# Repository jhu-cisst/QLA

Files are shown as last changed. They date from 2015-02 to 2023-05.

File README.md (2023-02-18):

# QLA
Design files for Quad Linear Amplifier (QLA) board

* `QLA.PrjPCB`: Altium Designer project file
* `Snn.SchDoc`: schematics (Altium Designer format)
* `Snn.Harness`: signal harnesses (Altium Designer format)
* `AMP.PcbDoc`: PCB layout (Altium Designer format)
* `QLA-Schematics.pdf`: PDF of schematics
* `QLA-BOM.xls`: Bill of Materials (Microsoft Excel format)
* `QLA-HeatSink.pdf`: PDF of heat sink drawing
* `QLA-PCB-Fabrication.zip`: PCB fabrication (Gerber) files
* `QLA-Assembly.zip`: PCB assembly files (e.g., paste masks, pick-and-place)
 
## Release Notes

* Rev 1.1: Build #0 (5 board pilot run)
* Rev 1.2: Build #1 (44 boards)
  * Deleted trace from Q15A (MOSFET) to U39B (OPA549) to avoid glitches at power-up (on all 4 channels)
  * Added J11 to enable connection to remote LED panel
* Rev 1.3 (PCB silkscreen is Rev 1.2): Build #2 (68 boards), Build #3 (72 boards), Build #4 (80 boards)
  * Changed relay (U31) from +12V to +5V to avoid rework needed to bring external +12V to board
  * Fixed silkscreen for Pot2 and Pot3 test points (they were swapped)
  * Changed R52 to 0 Ohms (Rev 1.1 and 1.2 boards were reworked accordingly)
  * Added screwlocks (Female, 4-40, 0.185") to DB9 connector
  * Design files indicate Rev 1.3, but manufactured boards show Rev 1.2; boards can be distinguished by looking at relay (U31)
* Rev 1.4: Build #5 (92 boards)
  * Changed digital outputs from open-drain MOSFETs to bi-directional bus transceivers (74LVC2T45) with 5V output; direction controlled by FPGA IO1-5 and IO1-6. Proper operation requires FPGA Firmware Rev 5+
  * Added feedback of motor voltage fault (from LT4356) on FPGA IO1-7
  * Grounded heatsink on PCB
  * Added plated slots for soldering 68-pin connector tabs
  * Moved Q13, Q14 and updated PCB pads to facilitate assembly
* Rev 1.4a: Build #6 (75 boards)
  * Increased acceptable range of motor supply voltage from 11.2V-50.2V to 10.5V-52.7V (values are approximate)
    * Changed R33, R34 to raise LT4356 maximum voltage from ~51.25V to ~52.7V
    * Changed R27, R28 to set MV_GOOD window comparator thresholds to 10.5V and 52.8V
  * Added transorb SMAJ64CA on back side of connector J5, between pins 2 and 3, to limit flyback voltages on motor power supply (especially with 48V supply)
* Rev 1.4b: Build #7 (120 boards), Build #8 (80 boards)
  * Changed pot filter cutoff frequency from 60 Hz to 5 kHz
    * Changed R1-8 from 39.2K to 464 Ohm
    * Allows faster reading of multiplexed signals (SUJ pots)
  * Fixed description of Q9-11,15 (30V instead of 20V)
* Rev 1.5: Build #9 (2 prototypes)
  * Added (open loop) motor voltage control as a software-selectable alternative to the existing (analog closed loop) motor current control
  * Added 10 digital I/O via an I/O expander (U41, Max7317):
    * 4 digital outputs to select between motor voltage control (0) or motor current control (1) for each axis
    * 4 digital outputs to enable the follower OPA549 op amps that previously were always enabled
    * 1 digital input that indicates whether voltage is present on safety line
    * 1 digital input that can be used to measure the motor supply voltage
  * Increased analog filter cutoff frequency from 60 Hz to 42 kHz for motor current feedback to ADC
  * Added pads for transorb (D12) on back side of board (previously, was either not present or was soldered between connector pins)
  * Changes due to component availability issues:
    * Support use of 1 LTC2604 quad DAC instead of 4 LTC2601 single DACs; populate pulldown resistor R75 to indicate use of LTC2604
    * Support AD7694 as an alternative to LTC1864 ADC; this required the addition of voltage level translators (U44, U45)
    * Changed part number for 2.5V linear regulator (U32), which included a pinout change
    * Changed footprint for safety relay (U31)
    * Changed footprint for D7 (Schottky diode)
    * Several other part number changes that did not change pinout or package type
* Rev 1.6: Build #9 (98 boards)
  * Added tristate buffer (U46) to Max7317 output
  * Use OPA549 feedback cap (C74) for voltage control, in addition to current control, to prevent oscillation; increased C74 voltage rating from 16V to 100V and changed package from 0603 to 1206
  * Disconnected J2, pin 44, from GND (consistent with change to FPGA V3.1)

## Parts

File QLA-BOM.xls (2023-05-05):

 | Quad Linear Amplifier, Rev 1.6
 | Bill Of Materials
 | 2023-05-04
Revision: |  | 1.6
Seq | Qty. | Ref Des (Multi-4) | Description | Package | Manufacturer | Notes | Manufacturer Part # | Distributor | Distributor Part # | Avcon Part # | Est. Unit $ | Extended Cost
1 | 5 | C1-4, C92 | CAP, 0.047uF, 10%, 25V, X7R, 0603 | 0603 | Kemet | 2 | C0603C473K3RAC7867 | Digikey | 399-C0603C473K3RAC7867CT-ND | 022-4734-71/603 | 0.04 | 0.20
2 | 20 | C5-8, C65-68 | CAP, 1000pF, 5%, 50V, NPO, 0603 | 0603 | MuRata | 2 | GRM1885C1H102JA01D | Digikey | 490-1451-1-ND | 022-1026-61/603 | 0.02 | 0.48
3 | 14 | C9-10, C69-71 | CAP 0.01uF, 10%, 50V, X7R, 0603 | 0603 | Kemet | 2 | C0603C103K5RACTU | Digikey | 399-1091-1-ND | 022-1036-71/603 | 0.04 | 0.56
4 | 2 | C11-12 | CAP, 10uF 20%, 6.3V, X5R, 0603 | 0603 | TDK | 2 | C1608X5R0J106M080AB | Digikey | 445-4112-1-ND | 022-1061-81/603 | 0.32 | 0.64
5 | 2 | C13-14 | CAP, 1.0uF 10% 16V X7R, 0603 | 0603 | TDK | 2 | C1608X7R1C105K080AC | Digikey | 445-1604-1-ND | 022-1052-71/603 | 0.04 | 0.09
6 | 1 | C15 | CAP, 220pF, 5%, 50V, NPO, 0603 | 0603 | Kemet | 2 | C0603C221J5GACTU | Digikey | 399-1066-1-ND | 022-2216-61/603 | 0.14 | 0.14
7 | 1 | C16 | CAP, 0.022uF, 10%, 50V, X7R, 0603 | 0603 | TDK | 2 | C1608X7R1H223K080AA | Digikey | 445-1312-1-ND | 022-2236-71/603 | 0.03 | 0.03
8 | 3 | C17-19 | CAP, 47uF, 20%, 10V, Polymer Tantalum, Cap-B | CAP-B | AVX | NS | TCJB476M010R0070 | Digikey | 478-3132-1-ND | 022-4761-85SMB | 1.10 | 3.30
9 | 4 | C20-23 | CAP, 150uF, 20%, 6.3V, Polymer Tantalum, Cap-B | CAP-B | AVX | NS | TCJB157M006R0070 | Digikey | 478-4921-1-ND | 022-1570-85SMB | 2.48 | 9.92
10 | 3 | C24, C94-95 | CAP, 2.2uF, 20%, 100V, X7S, 1206 | 1206 | TDK | 2 | C3216X7S2A225M | Digikey | 445-5208-1-ND | 022-2267-81SM | 1.21 | 3.63
11 | 1 | C25 | CAP, 68uF 10%, 25V, Low ESR Tant. "SpeedPower" | CAP-D | Kemet | NS | T495X686K025ATE200 T495X686K025ZTE200 | Digikey | 399-3908-1-ND | 022-6864-75SMD | 1.69 | 1.69
12 | 5 | C26, C85 | CAP, 220uF, 20%, 63V, Alum, Low ESR, 10mm Radial | CAP-10MM | Rubycon | NS, 12 | 63YXJ220M10X20 |  |  | 022-2210-86 | 0.73 | 3.65
13 | 83 | C27-64, C75-82, C87-88, C93, C96-105 | CAP, 0.1uF 10% 16V X7R, 0603 | 0603 | Kemet | 2 | C0603C104K4RACTU | Digikey | 399-1096-1-ND | 022-1042-71/603 | 0.02 | 1.66
14 | 4 | C72 | CAP, 0.068uF 10% 16V X7R, 0603 (25V) | 0603 | Kemet | 2 | C0603C683K3RAC7867 | Digikey | 399-C0603C683K3RAC7867CT-ND | 022-6832-71/603 | 0.03 | 0.14
15 | 4 | C73 | CAP, 2.2uF 10% 6.3V X7R, 0603 | 0603 | MuRata | 2 | GCM188R70J225KE22D | Digikey | 490-5316-1-ND | 022-2250-71/603 | 0.45 | 1.80
16 | 12 | C83-84, C91 | CAP, 0.1uF, 10%, 100V, X7R, 0805 | 0805 | Kemet | 2 | C0805C104K1RACTU | Digikey | 399-3486-1-ND | 022-1047-71/805 | 0.35 | 4.20
17 | 8 | C74, C86 | CAP, 0.1uF, 10%, 100V, X7R, 1206 | 1206 | Kemet | 2 | C1206C104K1RACTU | Digikey | 399-1805-1-ND | 022-1047-71SM | 0.30 | 2.40
18 | 4 | C89 | CAP, 200pF, 10%, 10V+, X7R, 0603 (50V) | 0603 | Samsung | 2 | CL10B201KB8NNNC | Digikey | 1276-1982-1-ND |  | 0.02 | 0.06
19 | 4 | C90 | CAP, 100pF, 10%, 10V+, X7R, 0603 | 0603 | Samsung | 2 | CL10B101KB8NFNC | Digikey | 1276-1908-1-ND |  | 0.02 | 0.08
20 | 2 | D1-2 | LED, Dual, Red/Green | LED-3MM-QUAD | Kingbright | NS | WP130WCP/2EGW | Digikey | 754-1205-ND | 024-6382-00 | 0.97 | 1.94
21 | 1 | D3 | LED, Quad, Green | LED-3MM-QUAD | Kingbright | NS | WP914CK/4GDT | Digikey | 754-1286-ND | 024-6383-00 | 1.25 | 1.25
22 | 1 | D4 | DIODE, Dual Zener, 6.8V, SOT-23, DZ23C6V8 | SOT-23 | Vishay |  | AZ23C6V8-E3-08 | Mouser | 78-AZ23C6V8-E3-08 | 024-0514-SM | 0.15 | 0.15
23 | 2 | D5-6 | DIODE, 75V, 150mA, 1N4148WS, SOD-323 | SOD-323 | Diodes Inc. |  | 1N4148WS-7-F | Digikey | 1N4148WS-FDICT-ND | 024-0244-SM | 0.18 | 0.36
24 | 1 | D7 | DIODE, Schottky, 60V, 1A | SMP | Vishay |  | SS1P6L-M3/84A | Digikey | SS1P6L-M3/84AGICT-ND |  | 0.21 | 0.21
25 | 16 | D8-11 | DIODE, Schottky, 60V, 5A, PDS560 | PowerDI-5 | Diodes Inc. |  | PDS560-13 | Digikey | PDS560DICT-ND | 024-0362-SM | 1.36 | 21.76
26 | 1 | D12 | DIODE, TVS (Transorb) | SMA | Bourns | 2, 8 | SMAJ64CA | Mouser | 576-SMAJ64CA |  | 0.28 | 0.28
27 | 1 | D13 | DIODE, Zener, 36V, 1W | PowerDI-123 | Diodes Inc. |  | DFLZ36-7 | Digikey | DFLZ36-7DICT-ND |  | 0.30 | 0.30
28 | 2 | J1-2 | CONN, Header, 2x22 Pos, Vertical, 2MM. | HDR-22x2-2MM | Samtec |  | TMM-122-03-L-D | Samtec | TMM-122-03-L-D | 026-0846-00 | 2.00 | 4.00
29 | 1 | J3 | CONN, SCSI/VHDCI, 68 Pin, RA | CONN-VHDCI | TE Conn | NS | 5796055-1 | Mouser | 571-5796055-1 | 026-1137-00 | 15.88 | 15.88
30 | 1 | J4 | CONNECTOR, DB-9 Female, High Current | DB9F | Tyco | NS | 5205866-1 | Digikey | A32065-ND | 026-0862-00 | 17.04 | 17.04
31 | 1 | J5 | CONN, Receptacle, 4 Pos, 3.8mm Vertical | WM-BL381-4 | Weidmuller |  | 1793810000 | Digikey | 281-1959-ND | 026-1138-00 | 1.55 | 1.55
32 | 3 | J6-8 | CONN, Header, 2 Pos, Vertical 0.100 | TH | Tyco | 2 | 640456-2 | Digikey | A1921-ND | 026-0080-00 | 0.30 | 0.90
33 | 2 | J9-10 | CONN, Header, 3 Pos, Vertical 0.100 | TH | Tyco | 2 | 640456-3 | Digikey | A19470-ND | 026-0083-00 | 0.34 | 0.68
34 | 1 | J11 | CONN, Header, 2x6 Pos, Vertical, 2MM. | TH | Hirose |  | DF11-12DP-2DSA(24) | Digikey | H10233-ND | 026-0840-00 | 0.92 | 0.92
35 | 1 | L1 | INDUCTOR, 100uH 20%, 1.9A | DR127 | Cooper | NS | DR127-101-R | Digikey | 513-1038-1-ND | 023-0178-SM | 1.74 | 1.74
36 | 3 | Q1-2, Q12 | Transistor, NPN, 160V, MMBT5551L | SOT-23 | Diodes Inc. | 2 | MMBT5551-7-F | Digikey | MMBT5551-FDICT-ND | 024-1193-SM | 0.43 | 1.29
37 | 0 | Q3-4 | Designator not used |  |  |  |  |  |  |  | 0.00 | 0.00
38 | 4 | Q5-8 | MOSFET, Pair N/P-Chan, 50V, 115mA, BSS8402 | SC70-6 | Rohm | 13 | US6M2 | Mouser | 755-US6M2GTR | 024-2199-SM | 0.30 | 1.20
39 | 7 | Q9-11, Q15 | MOSFET, Dual N-Chan, 30V (20V) | SOT-363 | Vishay | 2, 9 | SQ1912EH | Digikey | Q1912EH-T1_GE3CT-ND | 024-2190-SM | 0.19 | 1.33
40 | 2 | Q13-14 | MOSFET, N-Chan, 100V, 160A (200A) | TO-263-7 | On Semi | 10 | FDB0300N1007L | Mouser | 512-FDB0300N1007L | 024-2197-SM | 4.47 | 8.94
41 | 8 | R1-8 | RES, 464, 1%, 1/10W, 0603 | 0603 | Generic | 2, 15 | RC0603FR-07464RL | Digikey | 311-464HRCT-ND |  | 0.01 | 0.08
42 | 12 | R9-12, R56, R76-79 | RES, 100, 1%, 1/10W, 0603 | 0603 | Generic | 2 |  | Digikey | 541-100HCT | 020-1000-51/603 | 0.04 | 0.48
43 | 10 | R13-22 | RES, 150, 1%, 1/10W, 0603 | 0603 | Generic | 2 |  | Digikey | 541-150HCT | 020-1500-51/603 | 0.04 | 0.40
44 | 6 | R23-26, R68, R75 | RES, 1.00K, 1%, 1/10W, 0603 | 0603 | Generic | 2 |  | Digikey | 541-1.00KHCT | 020-1001-51/603 | 0.04 | 0.24
45 | 1 | R27 | RES, 127K, 1%, 1/10W, 0603 | 0603 | Generic | 2 |  | Digikey | 541-127KHCT | 020-1273-51/603 | 0.04 | 0.04
46 | 2 | R28-29 | RES, 4.02K, 1%, 1/10W, 0603 | 0603 | Generic | 2 |  | Digikey | 541-4.02KHCT | 020-4021-51/603 | 0.04 | 0.08
47 | 1 | R30 | RES, 2.21K, 1%, 1/10W, 0603 | 0603 | Generic | 2 |  | Digikey | 541-2.21KHCT | 020-2211-51/603 | 0.04 | 0.04
48 | 1 | R31 | RES, 8.87K, 1%, 1/10W, 0603 | 0603 | Generic | 2 |  | Digikey | 541-8.87KHCT | 020-8871-51/603 | 0.04 | 0.04
49 | 23 | R32, R40-44, R71-72 | RES, 10.0K, 1%, 1/10W, 0603 | 0603 | Generic | 2 |  | Digikey | 541-10.0KHCT | 020-1002-51/603 | 0.04 | 0.92
50 | 1 | R33 | RES, 2.43K, 0.1%, 1/10W, 0603 | 0603 | Generic | 2 |  | Digikey | RG16P2.43KBCT-ND |  | 0.36 | 0.36
51 | 1 | R34 | RES, 100K, 0.1%, 1/10W, 0603 | 0603 | Generic | 2 |  | Digikey | RG16P100KBCT-ND |  | 0.34 | 0.34
52 | 1 | R35 | RES, 1.00M, 1%, 1/10W, 0603 | 0603 | Generic | 2 |  | Digikey | 541-1.00MHCT | 020-1004-51/603 | 0.04 | 0.04
53 | 2 | R36-37 | RES, 10.0, 1%, 1/10W, 0603 | 0603 | Generic | 2 |  | Digikey | 541-10.0HCT | 020-1009-51/603 | 0.04 | 0.08
54 | 2 | R38-39 | RES, 0.006, 1%, 1W, 2512 | R2512 | Yageo |  | PF2512FKF070R006L | Digikey | 311-0.006AGCT-ND | 020-6007-54/251 | 0.88 | 1.76
55 | 16 | R45-46, R54-55 | RES, 26.7K, 1%, 1/10W, 0603 | 0603 | Generic | 2 |  | Digikey | 541-26.7KHCT | 020-2672-51/603 | 0.04 | 0.64
56 | 8 | R47, R49 | RES, 182K, 1%, 1/10W, 0603 | 0603 | Generic |  |  | Digikey | P182KHCT-ND |  | 0.02 | 0.15
57 | 6 | R48, R52-53 | RES, 4.99K, 1%, 1/10W, 0603 | 0603 | Generic | 2 |  | Digikey | 541-4.99KHCT | 020-4991-51/603 | 0.04 | 0.24
58 | 8 | R50-51 | RES, 62.0, 0.1%, 1/10W, 0603 | 0603 | Susumu | NS | RG1608P-620-B-T5 | Digikey | RG16P62.0BCT-ND | 020-6209-21/603 | 0.53 | 4.24
59 | 9 | R57-58, R69 | RES, 20.0K, 1%, 1/10W, 0603 | 0603 | Generic | 2 |  | Digikey | 541-20.0KHCT | 020-2002-51/603 | 0.04 | 0.36
60 | 8 | R59-60 | RES, 20.0K, 0.1%, 1/10W, 0603 | 0603 | Susumu | 2 | RG1608P-203-B-T5 | Digikey | RG16P20.0KBCT-ND | 020-2002-21/603 | 0.40 | 3.20
61 | 4 | R61 | RES, 6.04K, 1%, 1/10W, 0603 | 0603 | Generic | 2 |  | Digikey | 541-6.04KHCT | 020-6041-51/603 | 0.04 | 0.16
62 | 4 | R62 | RES, 0.20 Ohm, 1%, 30W, TO-220 | TO-220 | Caddock | 3 | MP930-0.20-1% | Digikey | MP930-0.20F-ND | 020-2009-50 | 5.23 | 20.92
63 | 4 | R63 | RES, 4.7, 5%, 1/2W, Carbon Composite | R-1/2W | TE Conn | 2 | CBT50J4R7 | Mouser | 279-CBT50J4R7 | 020-4708-63 | 0.22 | 0.88
64 | 4 | R64-67 | RES, 100, 1%, 1/4W, 1206 | 1206 | Generic | 2 |  | Digikey | 541-100FCT | New Part | 0.04 | 0.16
65 | 1 | R70 | RES, 1.5K, 5%, 1/2W, 0805 | 0805 | Generic | 2 | ERJ-P06J152V | Digikey | P1.5KADCT-ND |  | 0.04 | 0.04
66 | 2 | R73-74 | RES, 49.9K, 1%, 1/10W, 0603 | 0603 | Generic |  |  | Digikey | RMCF0603FT49K9CT-ND |  | 0.01 | 0.01
67 | 5 | RN1-5 | RES ARRAY, 1.0K, 4 DIS, 5%, SM 0.032 | R-SM-8/32 | CTS | 2 | 742C083102JPTR | Digikey | 742C083102JPCT-ND | 020-1001-6RASM | 0.02 | 0.10
68 | 7 | RN6-9, RN13-15 | RES ARRAY, 10K, 4 DIS, 5%, SM 0.032 | R-SM-8/32 | CTS | 2 | 742C083103JPTR | Digikey | 742C083103JPCT-ND | 020-1002-6RASM | 0.02 | 0.14
69 | 3 | RN10-12 | RES ARRAY, 100, 4 DIS, 5%, SM 0.032 | R-SM-8/32 | CTS | 2 | 742C083101JPTR | Digikey | 742C083101JPCT-ND | 020-1000-6RASM | 0.02 | 0.06
70 | 1 | U1 | IC, EEPROM, 128Kbit, 25xx128 (xx=AA or LC) | TSSOP-8 | Microchip |  | 25xx128-I/ST (xx=AA or LC) | Digikey | 25LC128T-I/STCT-ND | 024-2620-SM | 1.14 | 1.14
71 | 1 | U2 | IC, Dual Power Switch, 500mA, TPS2046 | SO-8 | TI |  | TPS2046BDR | Digikey | 296-17246-1-ND | 024-3614-SM | 2.07 | 2.07
72 | 6 | U3-4, U36 | IC, Op-Amp, Dual | MSOP-8 | Microchip | 14 | MCP6V87T-E/MS | Digikey | 150-MCP6V87T-E/MSCT-ND | 024-6327-SM | 1.52 | 9.09
73 | 8 | U5-8, U34 | IC, ADC, 16 Bit | MSOP-8 | Analog Devices | 16 | AD7694xRM[Z] (x=A or B) | Digikey | AD7694ARMZ-ND |  | 15.19 | 121.48
74 | 4 | U9-10, U13-14 | IC, Dual Schmit Trig. Buffer, 5V Input, 74LVC2G17 | SOT-23-6 | On Semi | 2 | SN74LVC2G17DBVR | Digikey | 296-13012-1-ND | 024-3615-SM | 0.66 | 2.64
75 | 4 | U11-12, U44-45 | IC, 2-bit, Bus tranceiver/translator, 74LVC2T45 | US-8 | TI |  | SN74LVC2T45DCUR | Digikey | 296-17014-1-ND | New Part | 0.70 | 2.80
76 | 1 | U15 | IC, Linear Regulator, 4.5V, 150mA, LP2985A-4.5 | SOT-23-5 | National Semi. |  | LP2985AIM5-4.5/NOPB | Digikey | LP2985AIM5-4.5CT-ND | 024-2200-SM | 1.06 | 1.06
77 | 6 | U16-21 | IC, Quad Differential Receiver, AM26LV32 | SO-16 | TI |  | AM26LV32CD | Digikey | 296-6794-5-ND | 024-3618-SM | 1.34 | 8.04
78 | 1 | U22 | IC, Dual Comparator & Reference, LT6700-1 | SOT-23-6 | Linear Tech. | 1 | LT6700CS6-1#PBF | Linear Tech. | LT6700CS6-1#PBF | 024-2201-SM | 2.15 | 2.15
79 | 0 | U23-26 | IC, DAC, 16 Bit, Mid-Scale Startup, LTC2601-1 | DFN-10 | Linear Tech. | 1, 15 | LTC2601CDD-1#PBF | Linear Tech. | LTC2601CDD-1#PBF | 024-3616-SM | 3.60 | 0.00
80 | 1 | U27 | IC, Step Down DC-DC converter, 1.5A, LT1766 | TSSOP-16 | Linear Tech. | 1 | LT1766EFE#PBF | Linear Tech. | LT1766EFE#PBF | 024-2622-SM | 5.36 | 5.36
81 | 1 | U28 | IC, Over-Voltage Protection IC, LT4356-1 | MSOP-10 | Linear Tech. | 1 | LT4356CMS-1#PBF | Linear Tech. | LT4356CMS-1#PBF | 024-9188-SM | 5.36 | 5.36
82 | 2 | U29-30 | IC, Temperature to Frequency Converter, MAX6576 | SOT-23-6 | Maxim |  | MAX6576ZUT+T | Digikey | MAX6576ZUT+TTR-ND | 024-9307-SM | 2.73 | 5.46
83 | 1 | U31 | RELAY, 5V, DPDT | DIP | TE Conn |  | IM03TS | Digikey | PB1094-ND |  | 3.44 | 3.44
84 | 4 | U32 | IC, Linear Regulator, LDO, 2.5V, AP7333-SR | SOT-23 | Diodes Inc. |  | AP7333-25SRG-7 | Mouser | 621-AP7333-25SRG-7 |  | 0.23 | 0.93
85 | 4 | U33 | IC, 2-Input AND Gate, Single, 74LVC1G08 | SC70-5 | TI |  | SN74LVC1G08DCK | Digikey | 296-11602-1-ND | 024-3613-SM | 0.53 | 2.12
86 | 4 | U35 | IC, Op-Amp, Single, OPA990S | SOT-23-6 | TI |  | OPA990SIDBVR | TI | OPA990SIDBVR | New Part | 0.71 | 2.84
87 | 4 | U37 | IC, Differential Amplifier, LT1990 | SO-8 | Linear Tech. | 1 | LT1990CS8#PBF | Linear Tech. | LT1990CS8#PBF | 024-6316-SM | 1.65 | 6.60
88 | 8 | U38-39 | IC, Power Amplifier, OPA549T | POWER-11-T | TI | 3 | OPA549T | Digikey | OPA549T-ND | 024-9313-00 | 20.40 | 163.20
89 | 4 | U40 | IC, Analog SPDT Switch, TS5A3159A | SOT-23-6 | TI |  | TS5A3159ADBVT | Digikey | 296-27121-1-ND | New Part | 0.67 | 2.67
90 | 1 | U41 | IC, SPI I/O Expander | QSOP-16 | Maxim |  | MAX7317AEE+ | Mouser | 700-MAX7317AEET | New Part | 3.07 | 3.07
91 | 1 | U42 | IC, Comparator, Single, LMV331M | SOT-23-5 | TI | 2 | LMV331M5X/NOPB | Digikey | LMV331M5X/NOPBCT-ND | New Part | 0.62 | 0.62
92 | 1 | U43 | IC, DAC, Quad, 16 Bit, Mid-Scale Startup, LTC2604-1 | SSOP-16 | Linear Tech. | 1, 15 | LTC2604CGN-1#PBF | Digikey | LTC26014IGN-1#PBF-ND | New Part | 18.98 | 18.98
93 | 1 | U46 | IC, Tri-state Buffer, 74AHC1G125 | SOT-23-5 | TI | 2 | SN74AHC1G125DBV | TI | SN74AHC1G125DBVR | New Part | 0.06 | 0.06
94 | 1 |  | HEATSINK, Rev 4 |  |  |  |  | Columbus Machine Works |  | 039-0368-00 | 56.40 | 56.40
95 | 1 |  | PCB, Quad Linear Amplifier, Rev 1.5 |  |  |  |  | Ohio Circuits |  | 027-0435-00 | 35.00 | 35.00
96 | 17 |  | SCREW, 4-40 X 3/8" Pan Head |  |  | 4, 5 |  | McMaster-Carr | 90272A108 | 039-0178-00 | 0.18 | 3.09
97 | 2 |  | LOCKWASHER, #4 Ext. Tooth, Zinc Plated |  |  | 5 |  | McMaster-Carr | 91114A005 | 039-0251-00 | 0.55 | 1.09
98 | 2 |  | HEX NUT, 4-40 UNC-2B Stainless |  |  | 5 |  | McMaster-Carr | 91240A005 | 039-0043-30 | 0.43 | 0.86
99 | 2 |  | SCREWLOCK, Female, 4-40, 0.185" |  | Tyco | 6 | 5747877-3 | Digikey | A35224-ND | 039-0381-00 | 0.68 | 1.35
100 | 2 |  | SCREWLOCK, Female, M2 |  | TE Conn | 11 | 787004-3 | Mouser | 571-7870043 |  | 1.55 | 3.10
101 | 8 |  | Washer, 1/8" ID, 1/4" OD, Type B |  |  | 4, 7 |  | McMaster-Carr | 92217A360 | 039-0435-00 | 0.42 | 3.40
 |  |  |  |  |  |  |  |  |  | Estimated total Cost: |  | $628.06
Notes:
 | ● | Reference designators highlighted in green are replicated 4 times on the PCB, as UxxA, UxxB, UxxC and UxxD.
 | ● | Text highlighted in red is highlighted to draw attention to the value/parameter and does not carry any special meaning.
 | ● | Component prices shown are the best guess at the time of updating this BOM, assuming Qty ~100 boards. Actual prices may be higher or lower depending upon a number of factors.
 | ● | Unless specified otherwise, the only substitutions allowed are substituting identical part number parts from a different manufacturer.
 | NS | No substitutions of any kind are allowed.
 | 1 | For Linear Tech parts, it is acceptable to substitute I (industrial temp), E (extended temp) or H (high temp) rated parts.
 |  | The suffixes "TRM" and "TR" signify tape and reel styles. Parts with suffix TRM, suffix TR can be substituted as needed.
 |  | Other than as specified above, no other substitutions are allowed.
 | 2 | Any component in an identical package that meets or exceeds all the paramaters specified in the description can be substituted.
 | 3 | The component must be installed to the heat sink or a heat sink template before being soldered to the board.
 |  | Use Thermal Heat Sink Compound Type 120, Avcom P/N 043-0018-00
 | 4 | For attaching components to Heat Sink
 | 5 | For attaching DB9 to PCB (Qty 2: Screw, Lockwasher, Hex nut)
 | 6 | Screwlocks for DB9 connector
 | 7 | For attaching OPA549 to heat sink when using 4-40 screws
 | 8 | Soldered on back side of board, near connector J5
 | 9 | Previously used 30V rated parts: NXP PMGD175XNE (Digikey P/N 1727-2695-1-ND) and PMGD370XN (Digikey P/N 568-2367-1-ND); another alternative is ON Semiconductor NTJD4001NT1G (Digikey P/N NTJD4001NT1GOSCT-ND)
 | 10 | Previously used Infineon IPB039N10N3 (Mouser P/N 726-IPB039N10N3G); other possibilities are Infineon IRLS4030TRL7PP and (higher rated) IPB065N15N
 | 11 | Screwlocks for VHDCI (68-pin) connector
 | 12 | Previously used United Chem, ELXZ630ELL221MJ25S (Digikey P/N 565-2040-ND)
 | 13 | Previously used Diodes Inc. BSS8402DW-7-F (Digikey P/N BSS8402DW-FDICT-ND)
 | 14 | Previously used Linear Tech LTC6081CMS8#PBF
 | 15 | Populate either U43 (LTC2604) and R75 or U23-U26 (LTC2601)
 | 16 | Previously used Linear Tech LTC1864CMS8#PBF (Avcom P/N 024-2621-SM)
Component Counts:
 | C | 180
 | D | 25
 | J | 11
 | L | 1
 | Q | 16
 | R | 145
 | RN | 15
 | U | 68

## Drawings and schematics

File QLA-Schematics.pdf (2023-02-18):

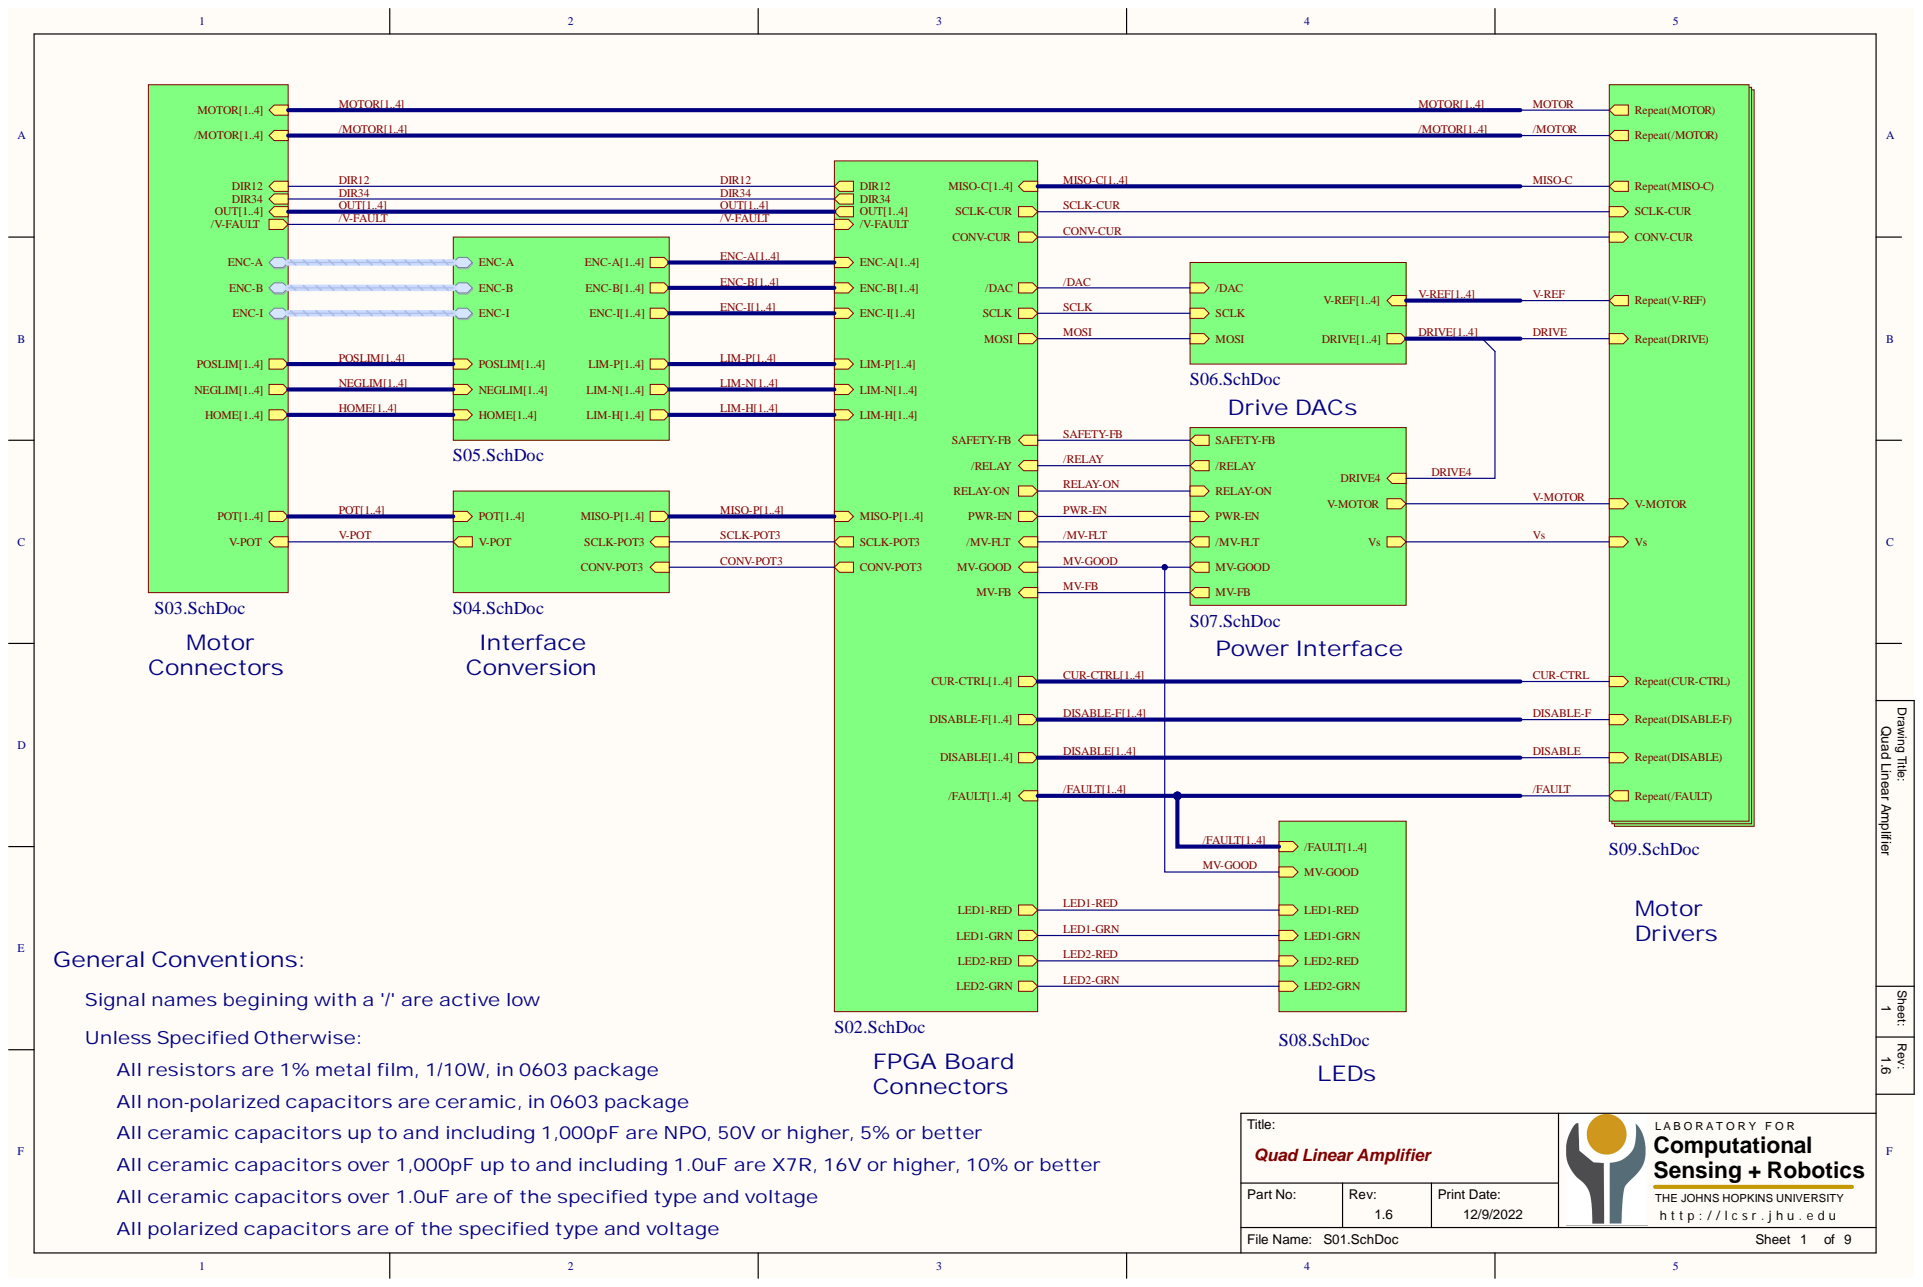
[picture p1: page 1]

ENC-I[1..4] | SCLK

POSLIM[1..4] | LIM-P[1..4] | MOSI

NEGLIM[1..4] | LIM-N[1..4] | S06.SchDoc Drive DACs

HOME[1..4] | LIM-H[1..4]

V-MOTOR

V-POT | SCLK-POT3 | /MV-FLT

CONV-POT3 | MV-GOOD

MV-FB | MV-GOOD MV-FB

Drawing Title: Rev: Sheet:

DISABLE-F[1..4] | | DISABLE-F

DISABLE[1..4] | | DISABLE

/FAULT[1..4] | | /FAULT

/FAULT[1..4]

LED1-RED | MV-GOOD

Signal names begining with a '/' are active low

Unless Specified Otherwise:
All resistors are 1% metal film, 1/10W, in 0603 package
All non-polarized capacitors are ceramic, in 0603 package
All ceramic capacitors up to and including 1,000pF are NPO, 50V or higher, 5% or better
All ceramic capacitors over 1,000pF up to and including 1.0uF are X7R, 16V or higher, 10% or better
All ceramic capacitors over 1.0uF are of the specified type and voltage
All polarized capacitors are of the specified type and voltage

Title: Quad Linear Amplifier | L A B O R A T O R Y F O R Computational Sensing + Robotics THE JOHNS HOPKINS UNIVERSITY h t t p : / / l c s r . j h u . e d u

Part No: | Rev: 1.6 | Print Date: 12/9/2022

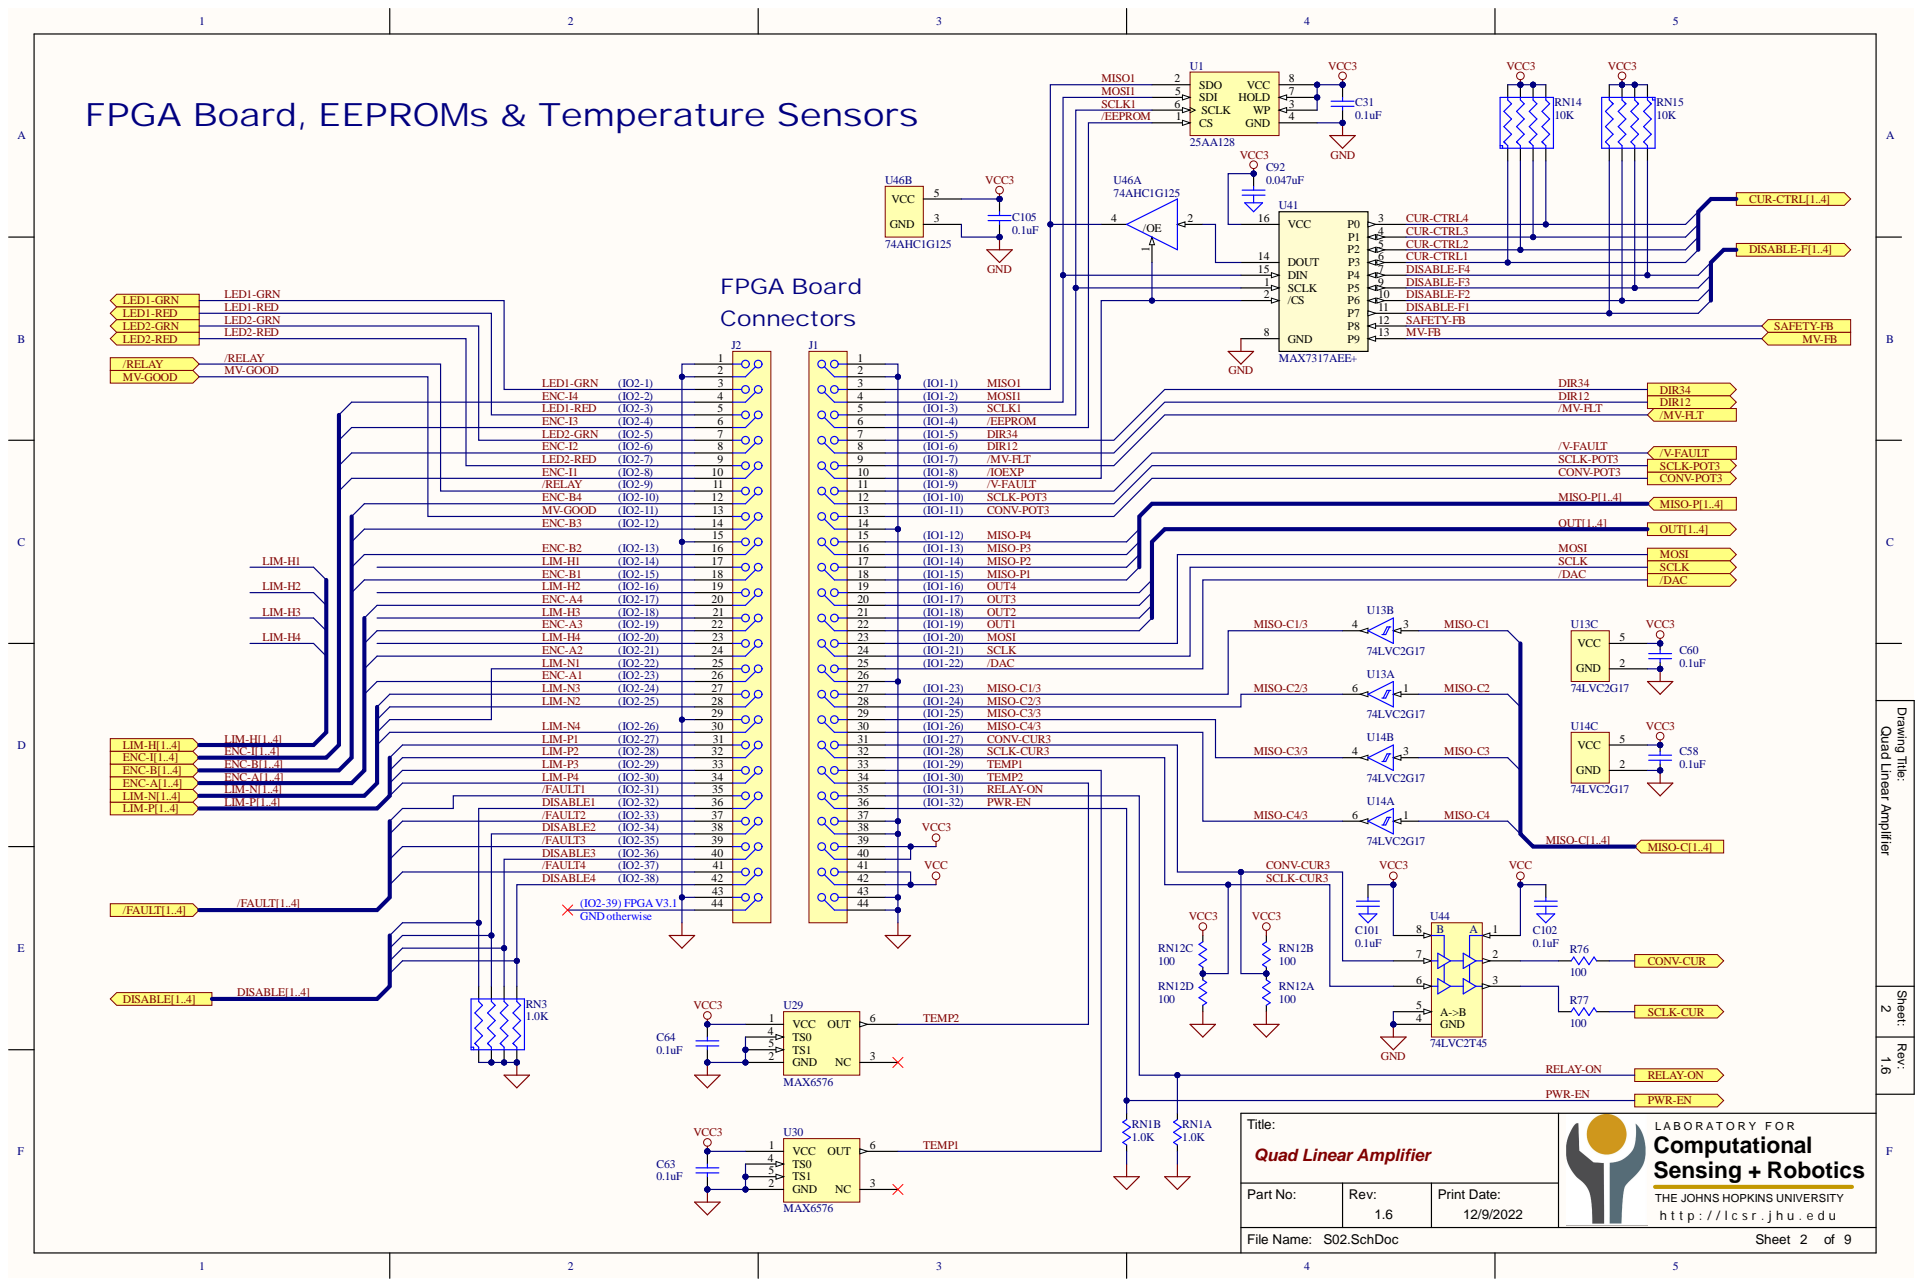
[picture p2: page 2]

Drawing Title: Rev: Sheet:

/FAULT3 (IO2-35) | | 39
DISABLE3 (IO2-36) | | 40
/FAULT4 (IO2-37) | | 41

RELAY-ON

TEMP1 | Title: Quad Linear Amplifier | L A B O R A T O R Y F O R Computational Sensing + Robotics THE JOHNS HOPKINS UNIVERSITY h t t p : / / l c s r . j h u . e d u

Part No: | Rev: 1.6 | Print Date: 12/9/2022

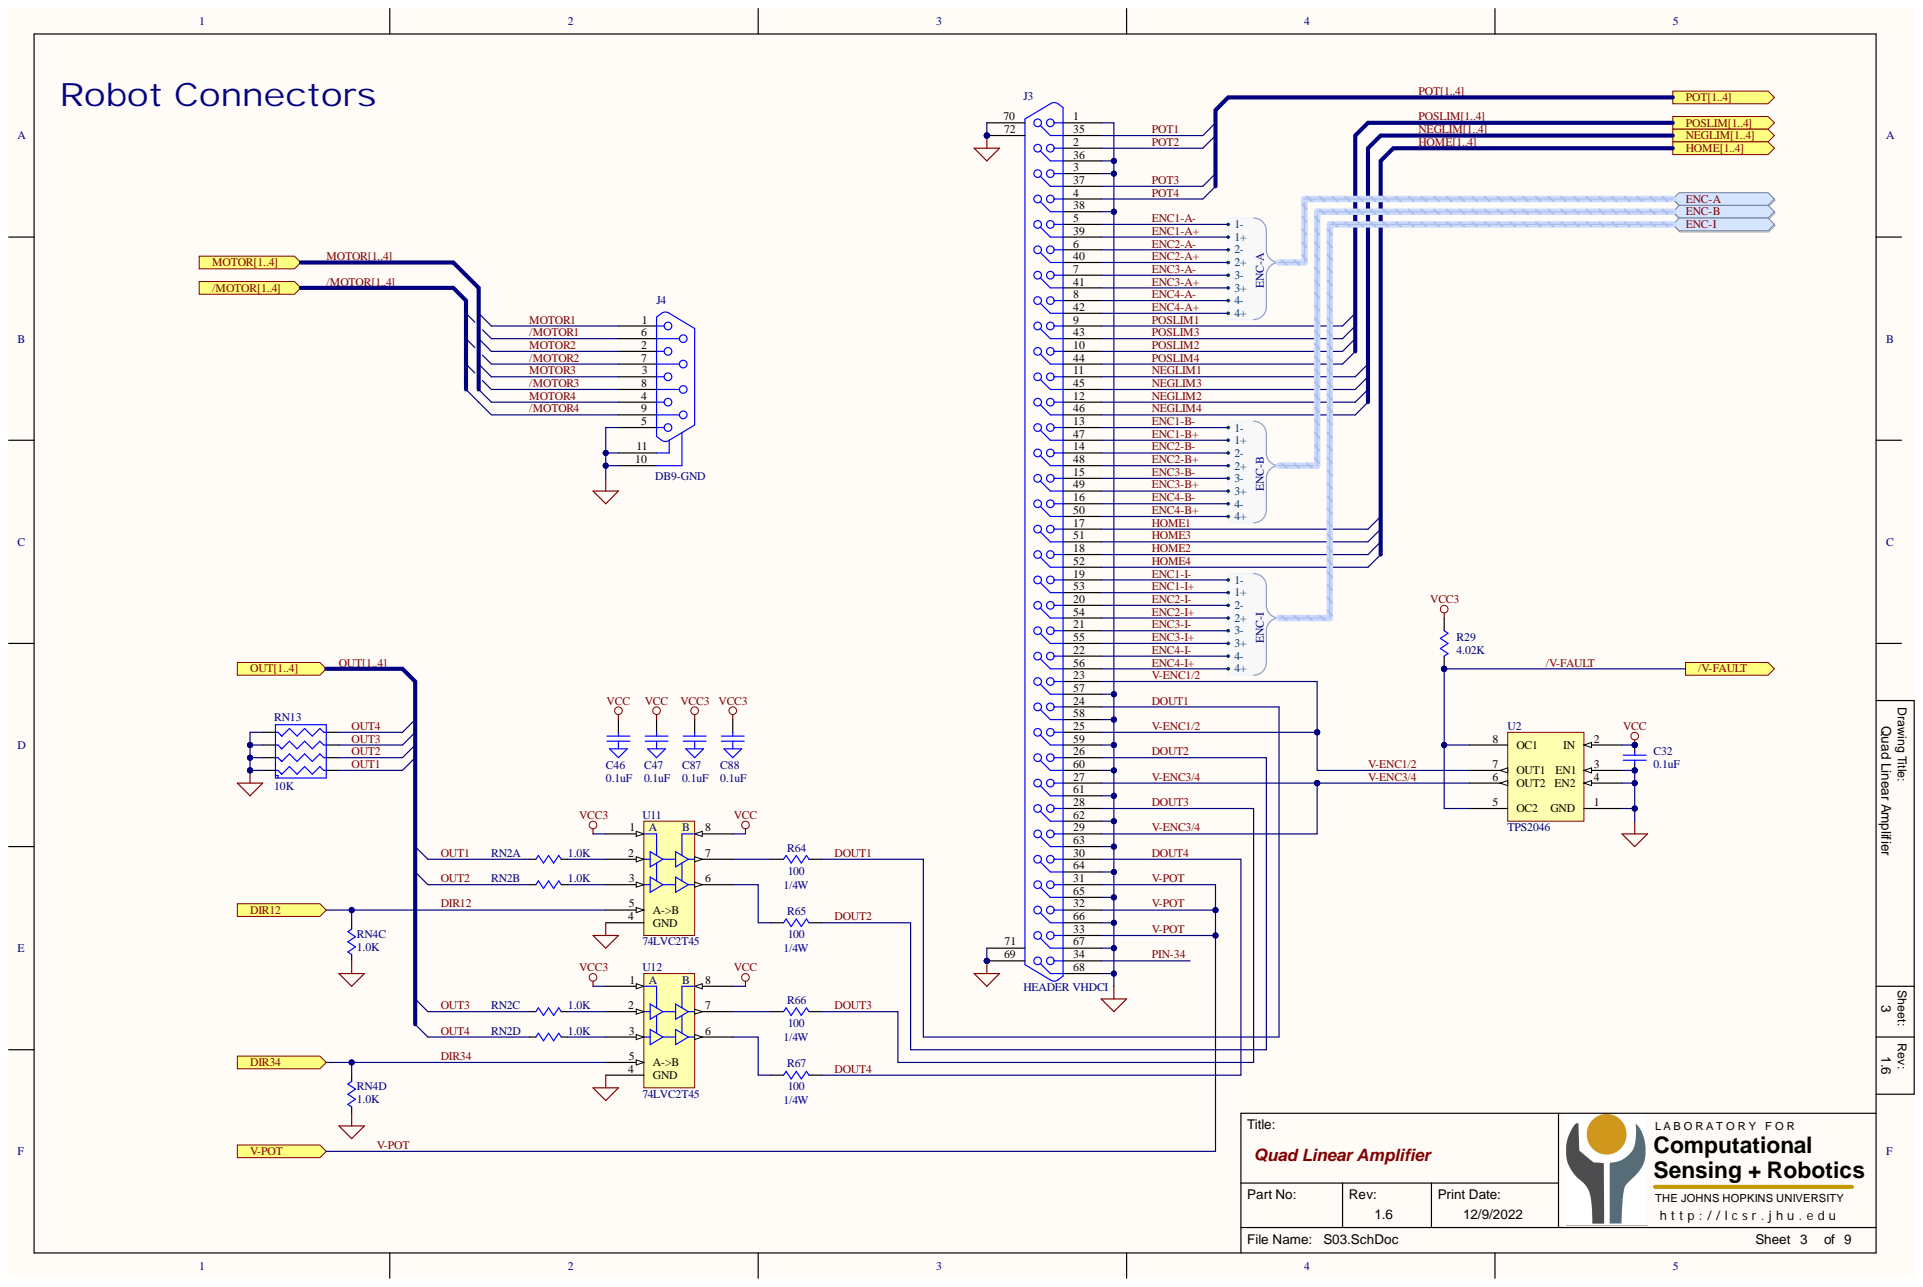
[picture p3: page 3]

43 10 | POSLIM3 POSLIM2

57 24 | | DOUT1

Drawing Title: Rev: Sheet:

58 25 | | V-ENC1/2

60 27 | V-ENC3/4

61 28 | | DOUT3

62 29 | | V-ENC3/4

63 30 64 31 | DOUT4

65 32 | V-POT

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

Part No: | Rev: 1.6 | Print Date: 12/9/2022

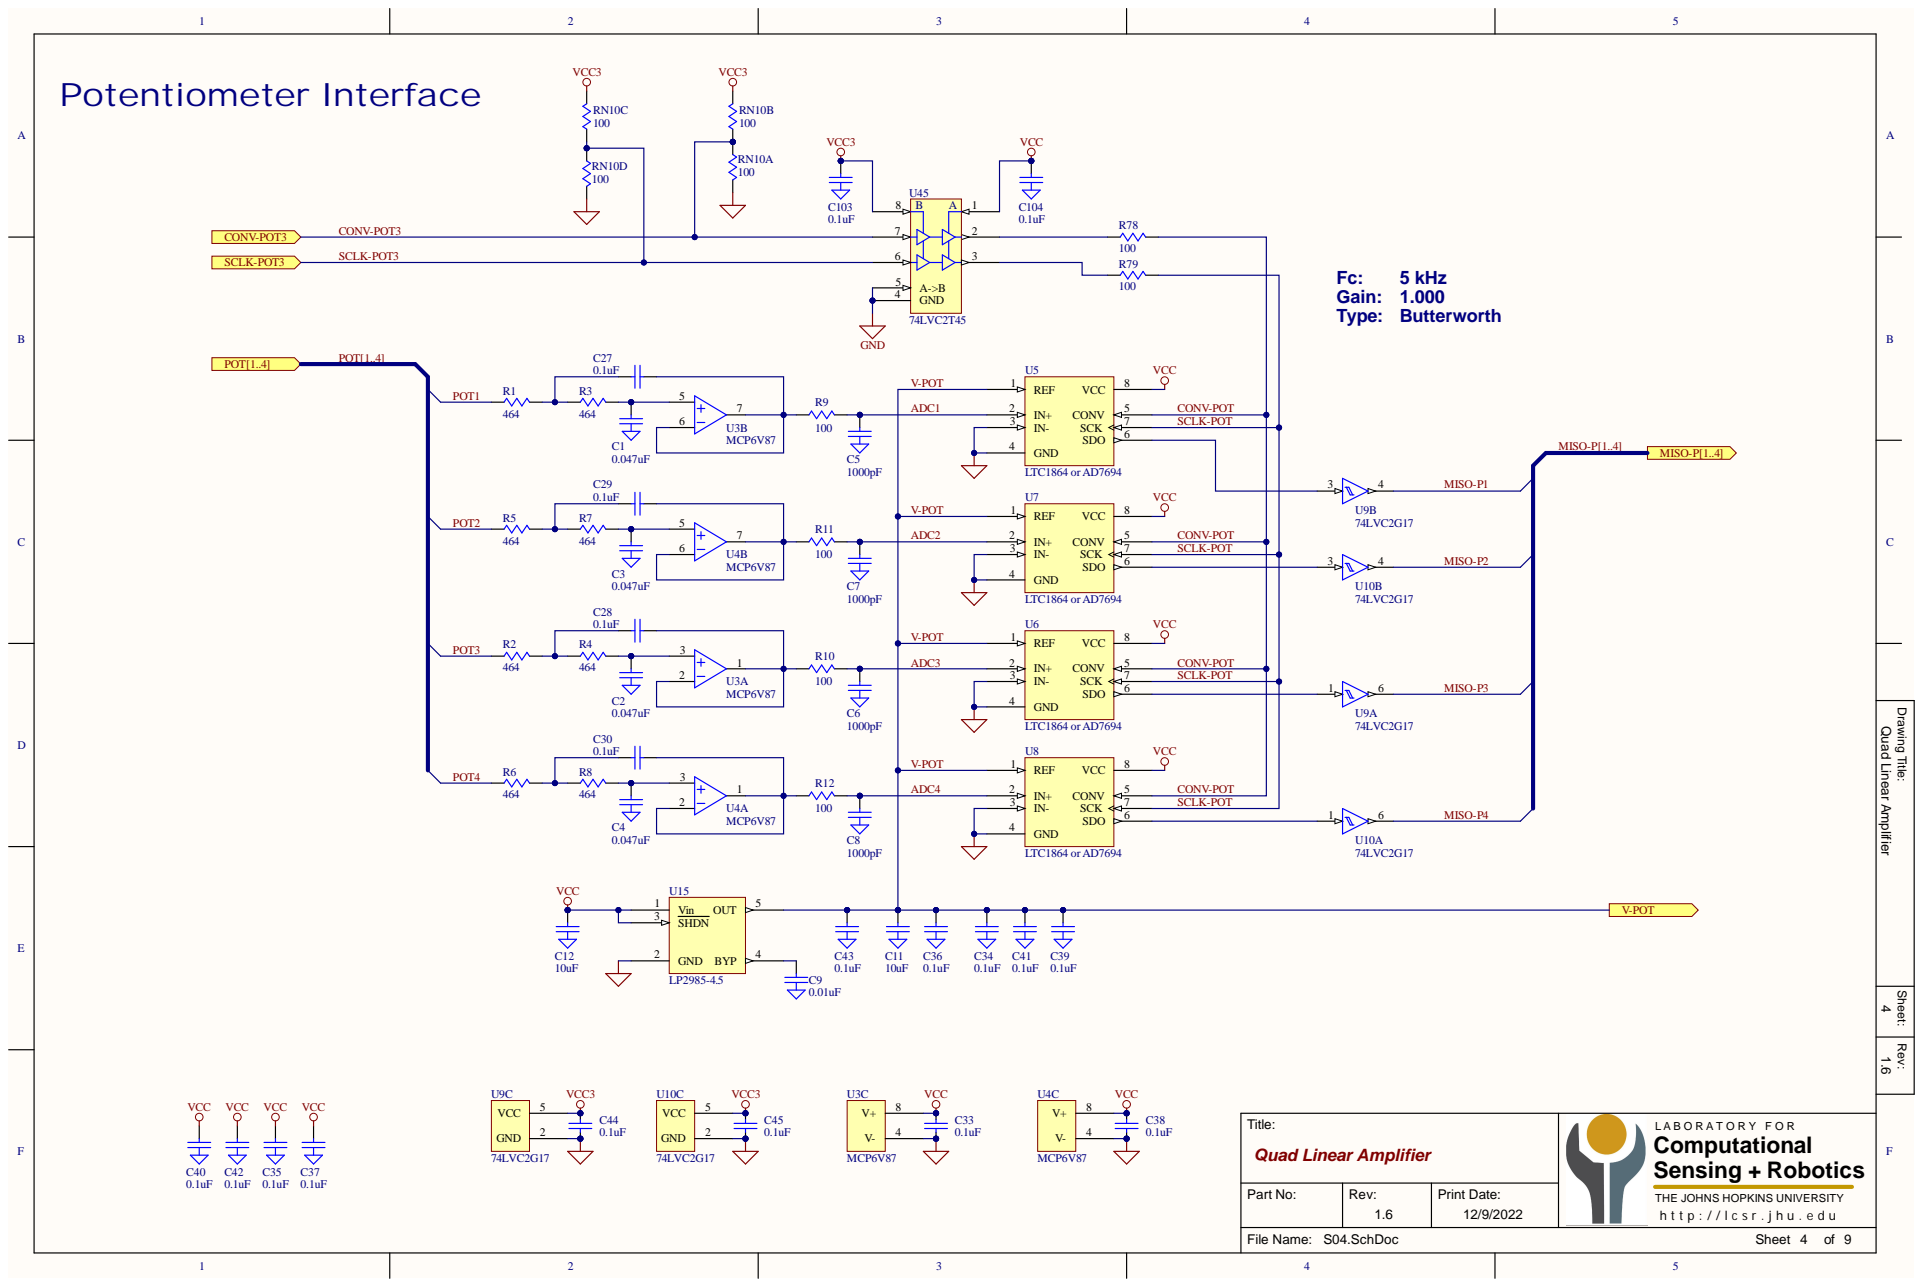
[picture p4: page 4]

Drawing Title: Rev: Sheet:

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

Part No: | Rev: 1.6 | Print Date: 12/9/2022

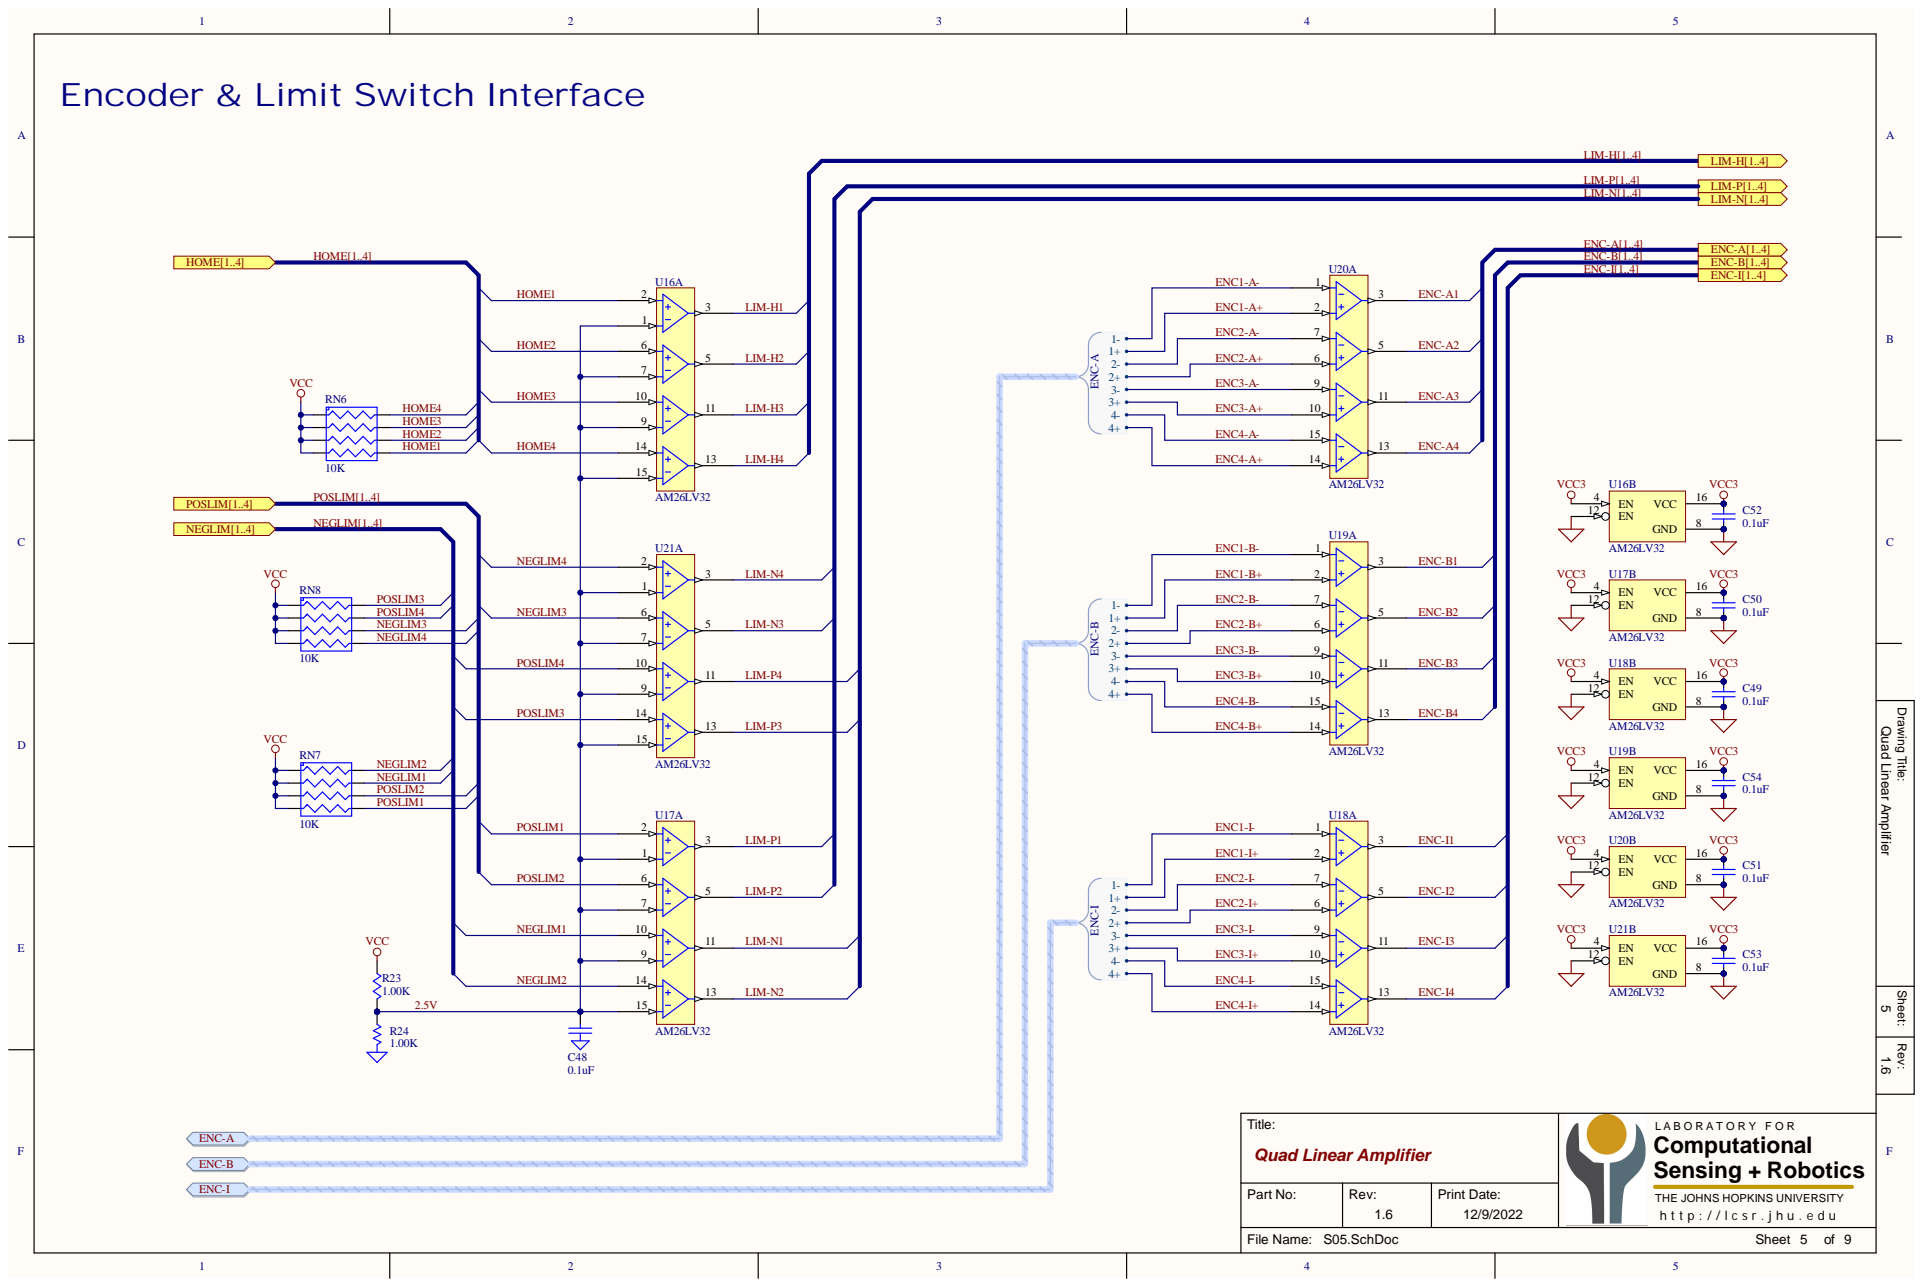
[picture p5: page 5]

Encoder & Limit Switch Interface

Drawing Title: Rev: Sheet:

Title: Quad Linear Amplifier | L A B O R A T O R Y F O R Computatio n a l Sensing + Robotics T H E J O H N S H O P K I N S U N I V E R S I T Y h t t p : / / l c s r . j h u . e d u

Par t No: | Rev : 1. 6 | P rint Date: 12/9/2022

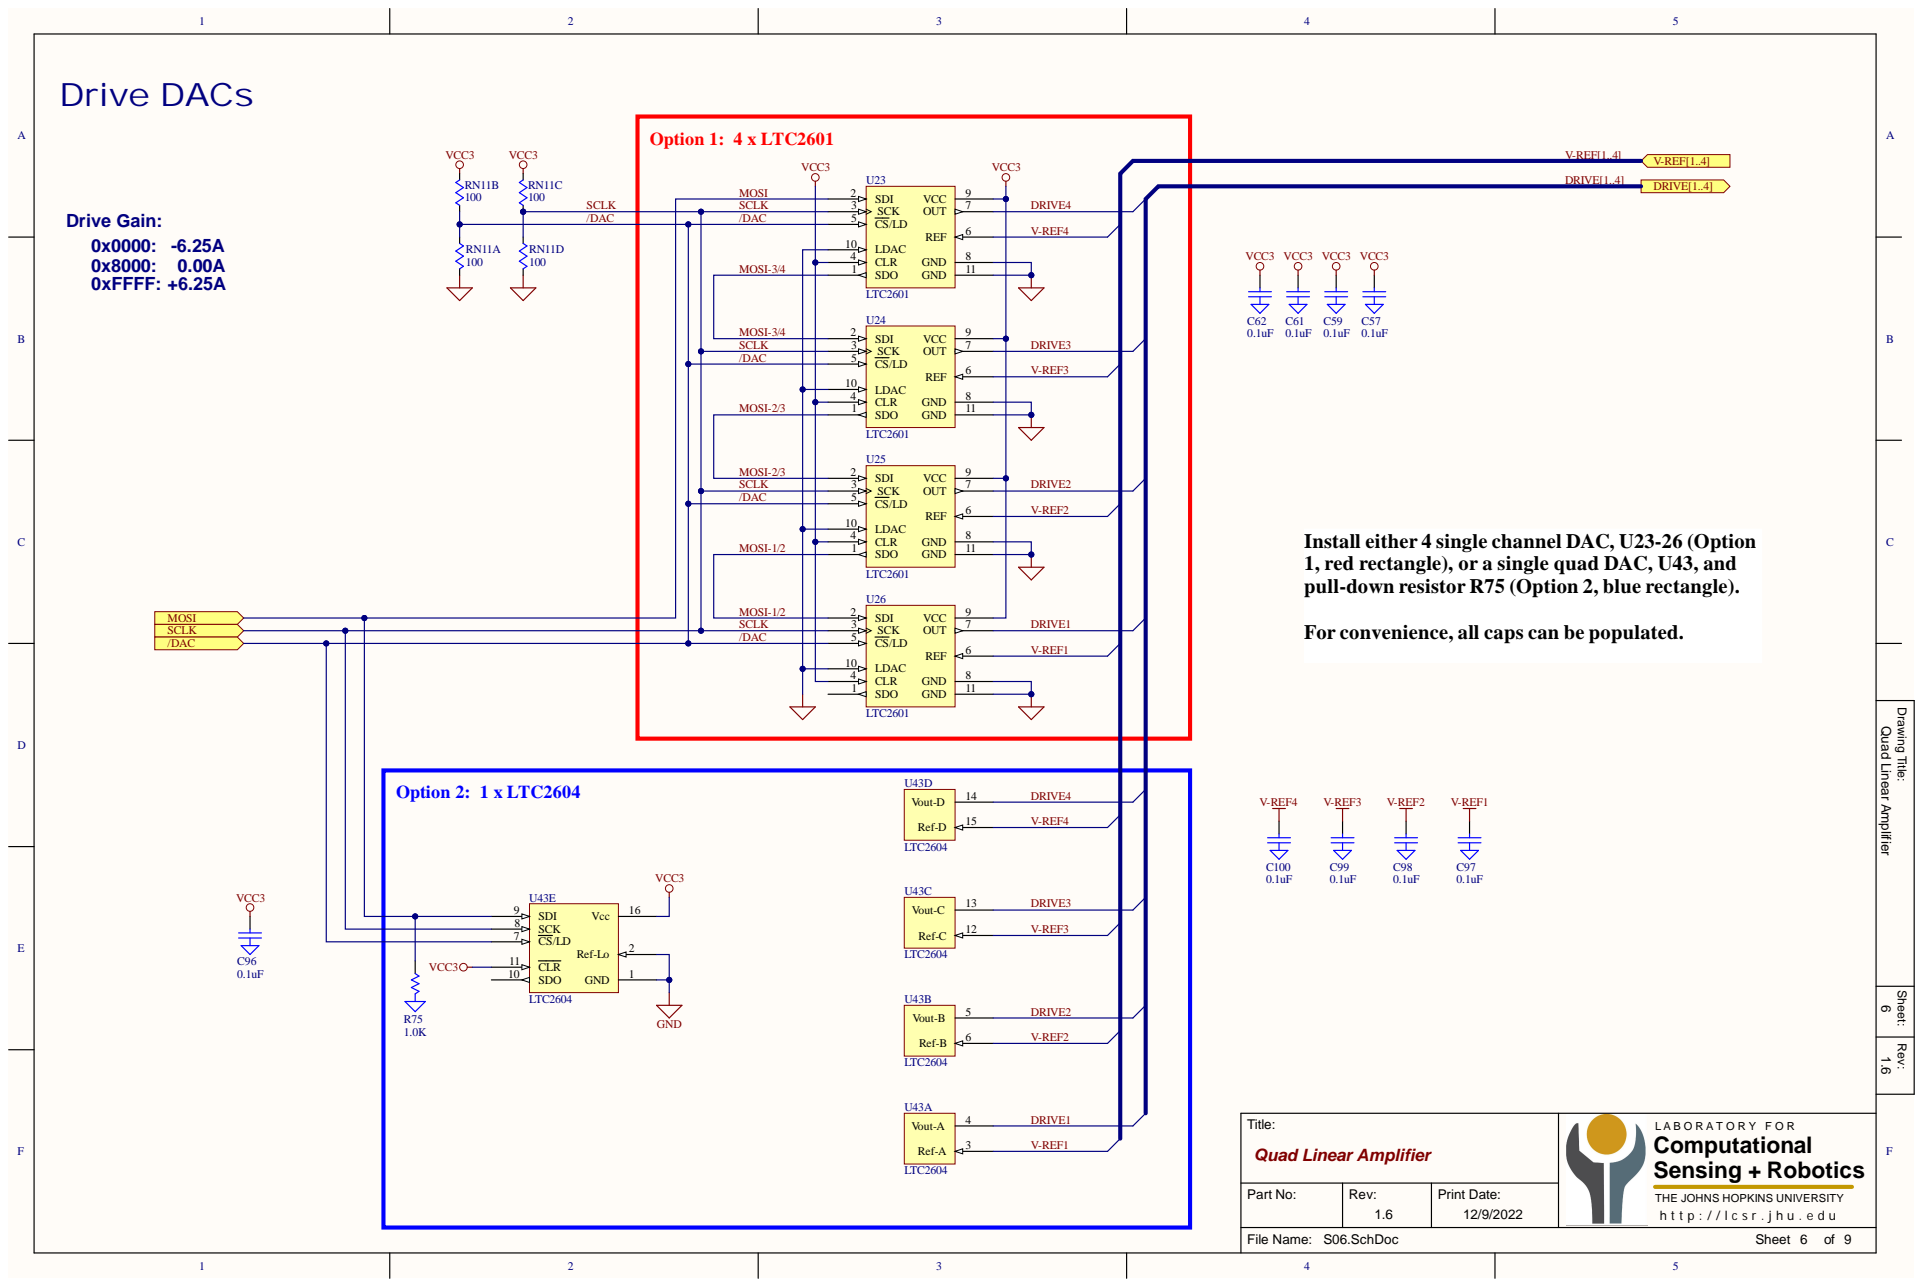
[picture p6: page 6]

LDAC 10
CLR 4

MOSI-3/4

MOSI-2/3 | LDAC 10

SDO 1

MOSI-2/3

MOSI-1/2 | LDAC 10

Install either 4 single channel DAC, U23-26 (Option
1, red rectangle), or a single quad DAC, U43, and
pull-down resistor R75 (Option 2, blue rectangle).

For convenience, all caps can be populated.

Drawing Title: Rev: Sheet:

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

Part No: | Rev: 1.6 | Print Date: 12/9/2022

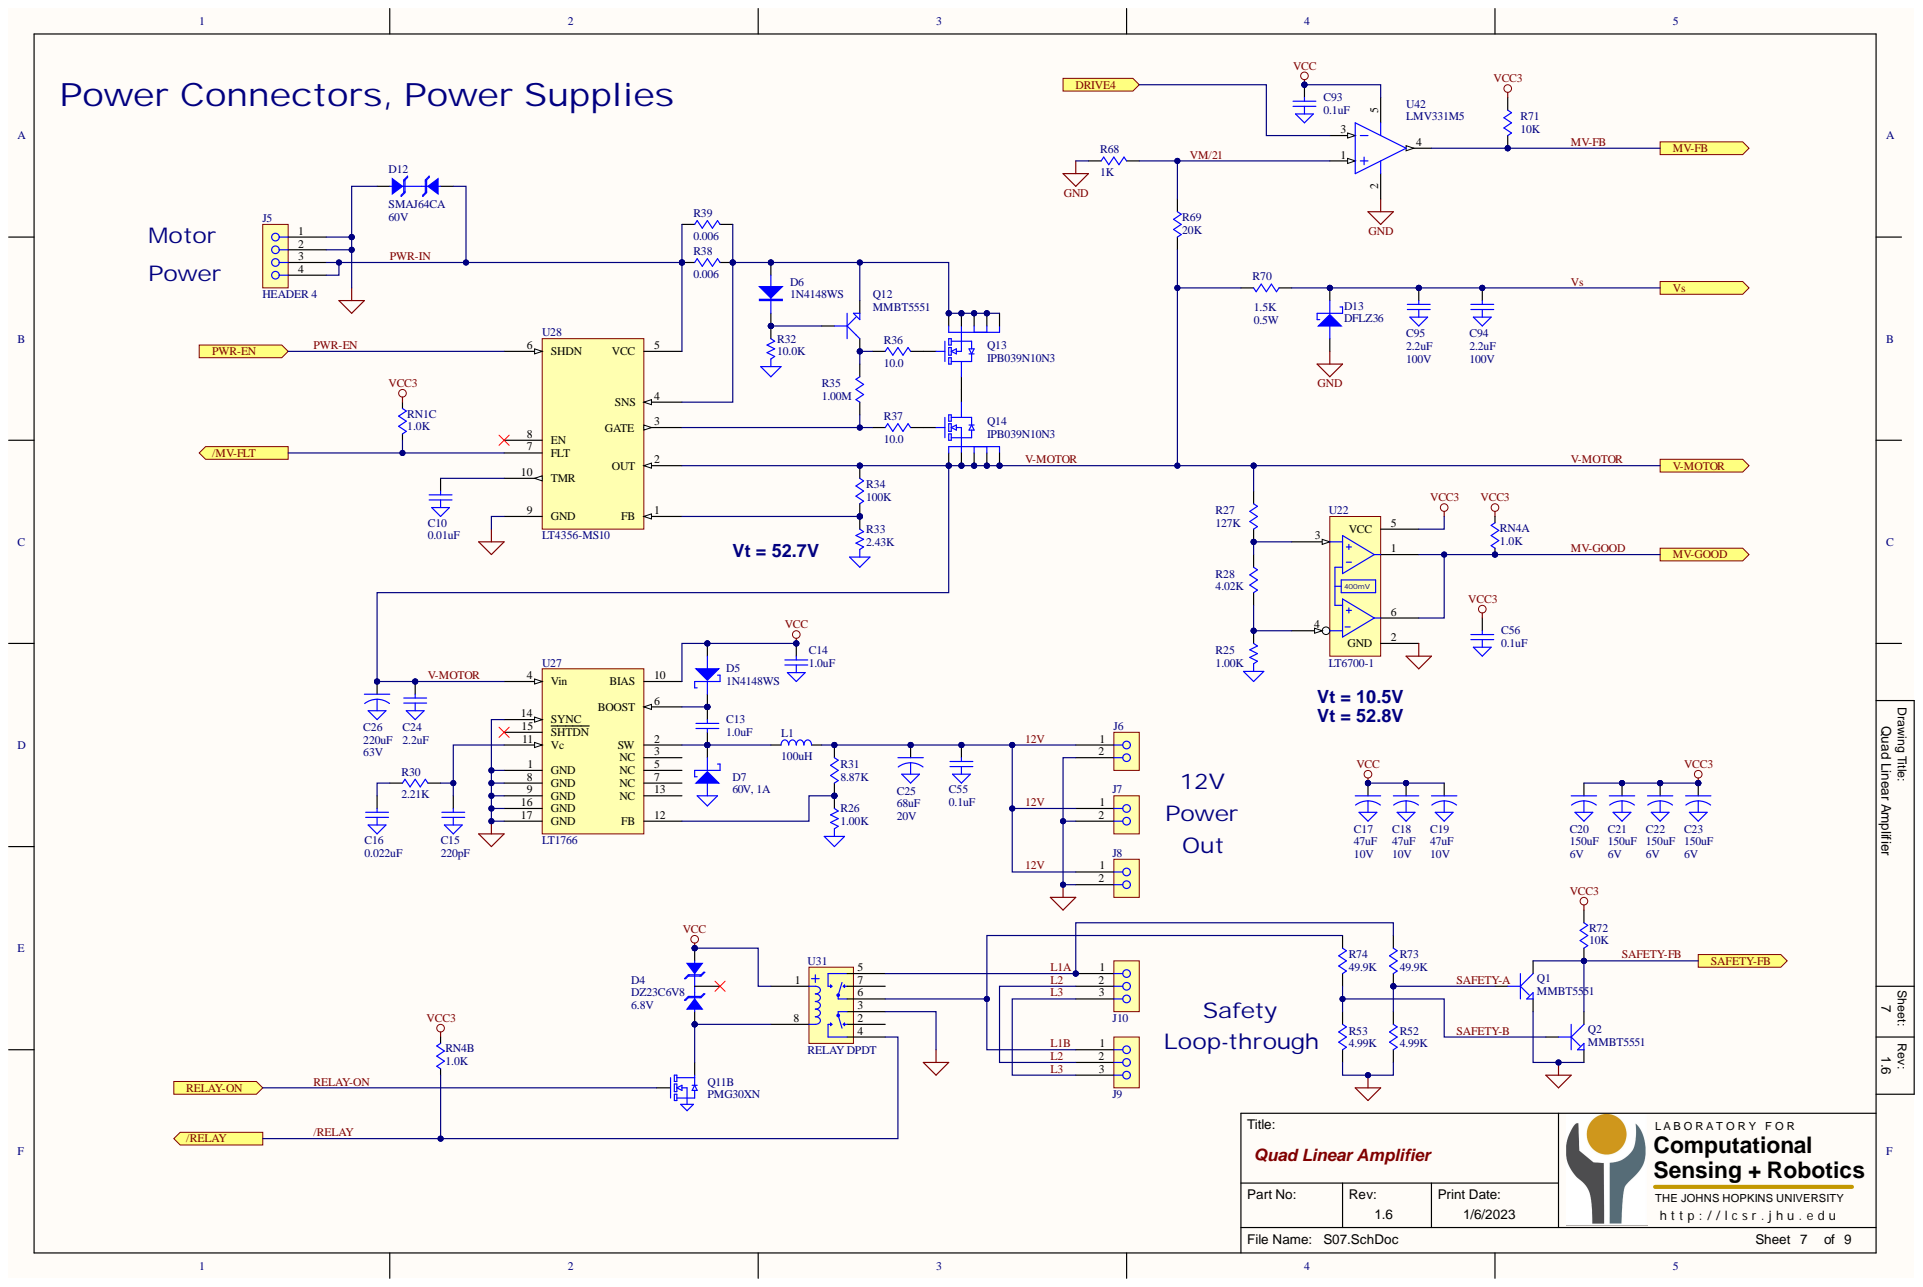
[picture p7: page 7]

Power Connectors, Power Supplies

PWR-IN

Drawing Title: Rev: Sheet:

L2 | 2
L3 | 3

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

Part No: | Rev: 1.6 | Print Date: 1/6/2023

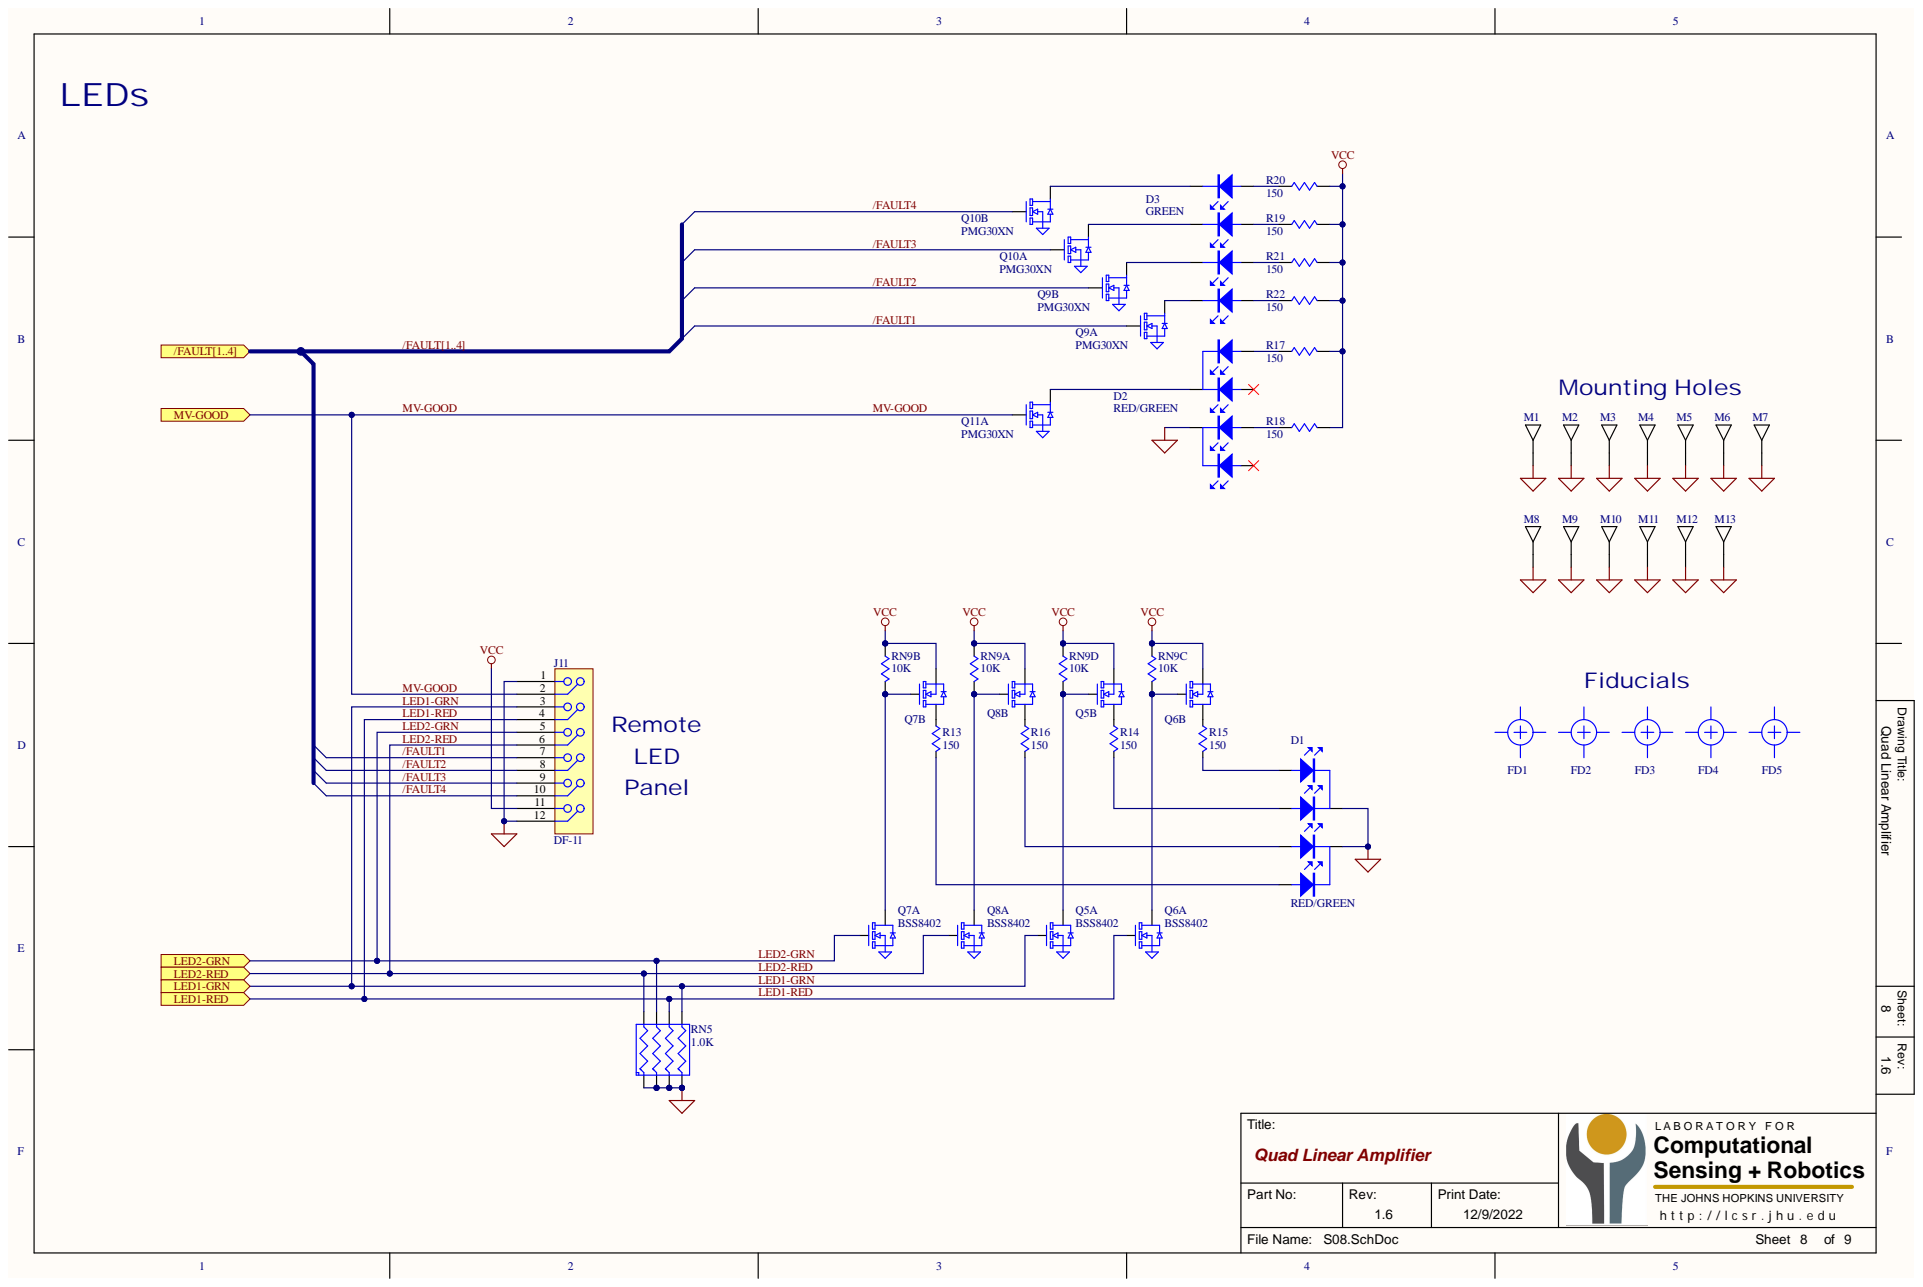
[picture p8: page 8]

Drawing Title: Rev: Sheet:

LED1-RED | 4 5

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

Part No: | Rev: 1.6 | Print Date: 12/9/2022

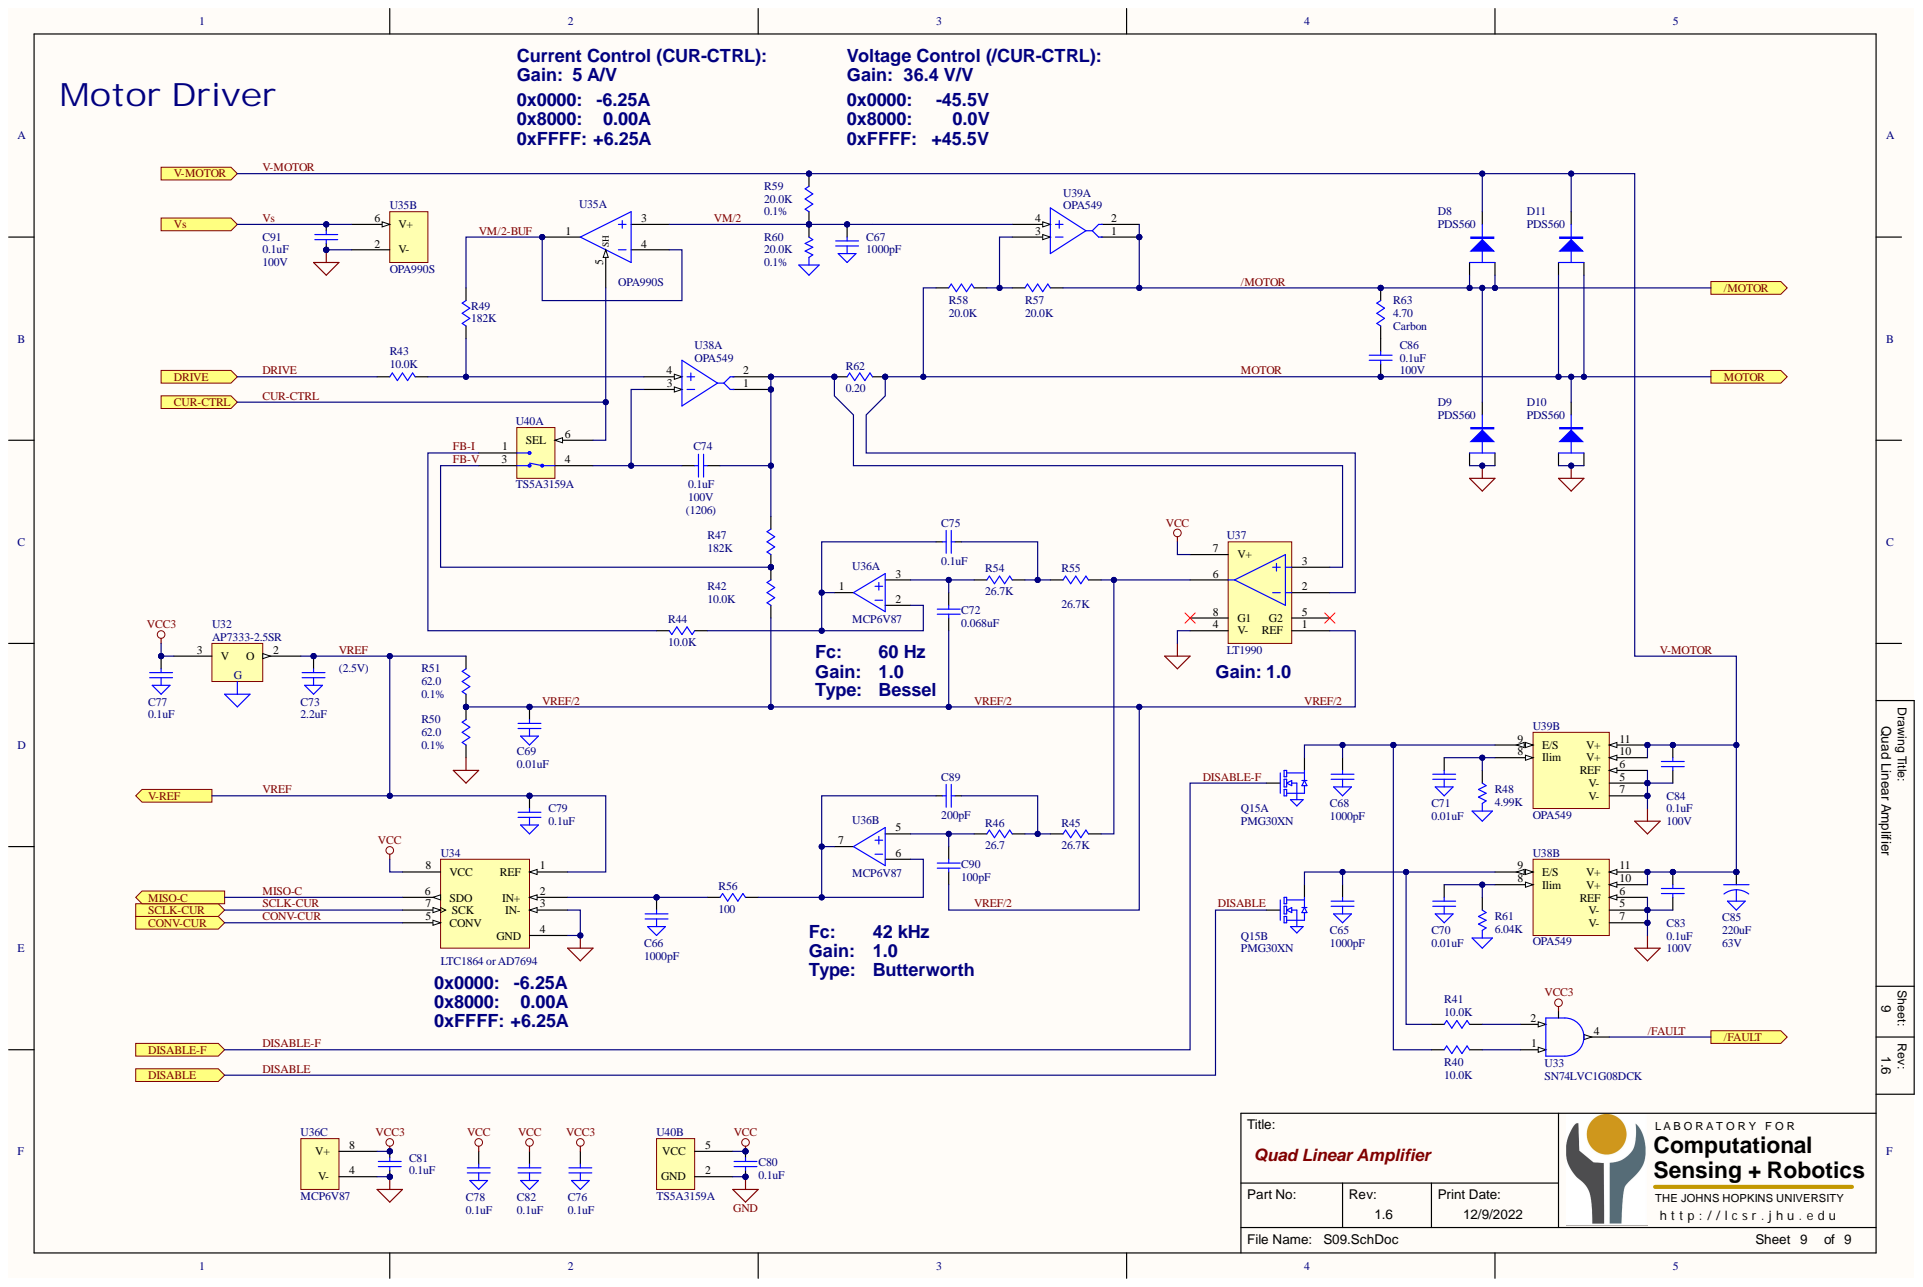
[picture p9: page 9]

Drawing Title: Rev: Sheet:

VREF | 26.7K | Q15A PMG30XN DISABLE

THE JOHNS HOPKINS UNIVERSITY

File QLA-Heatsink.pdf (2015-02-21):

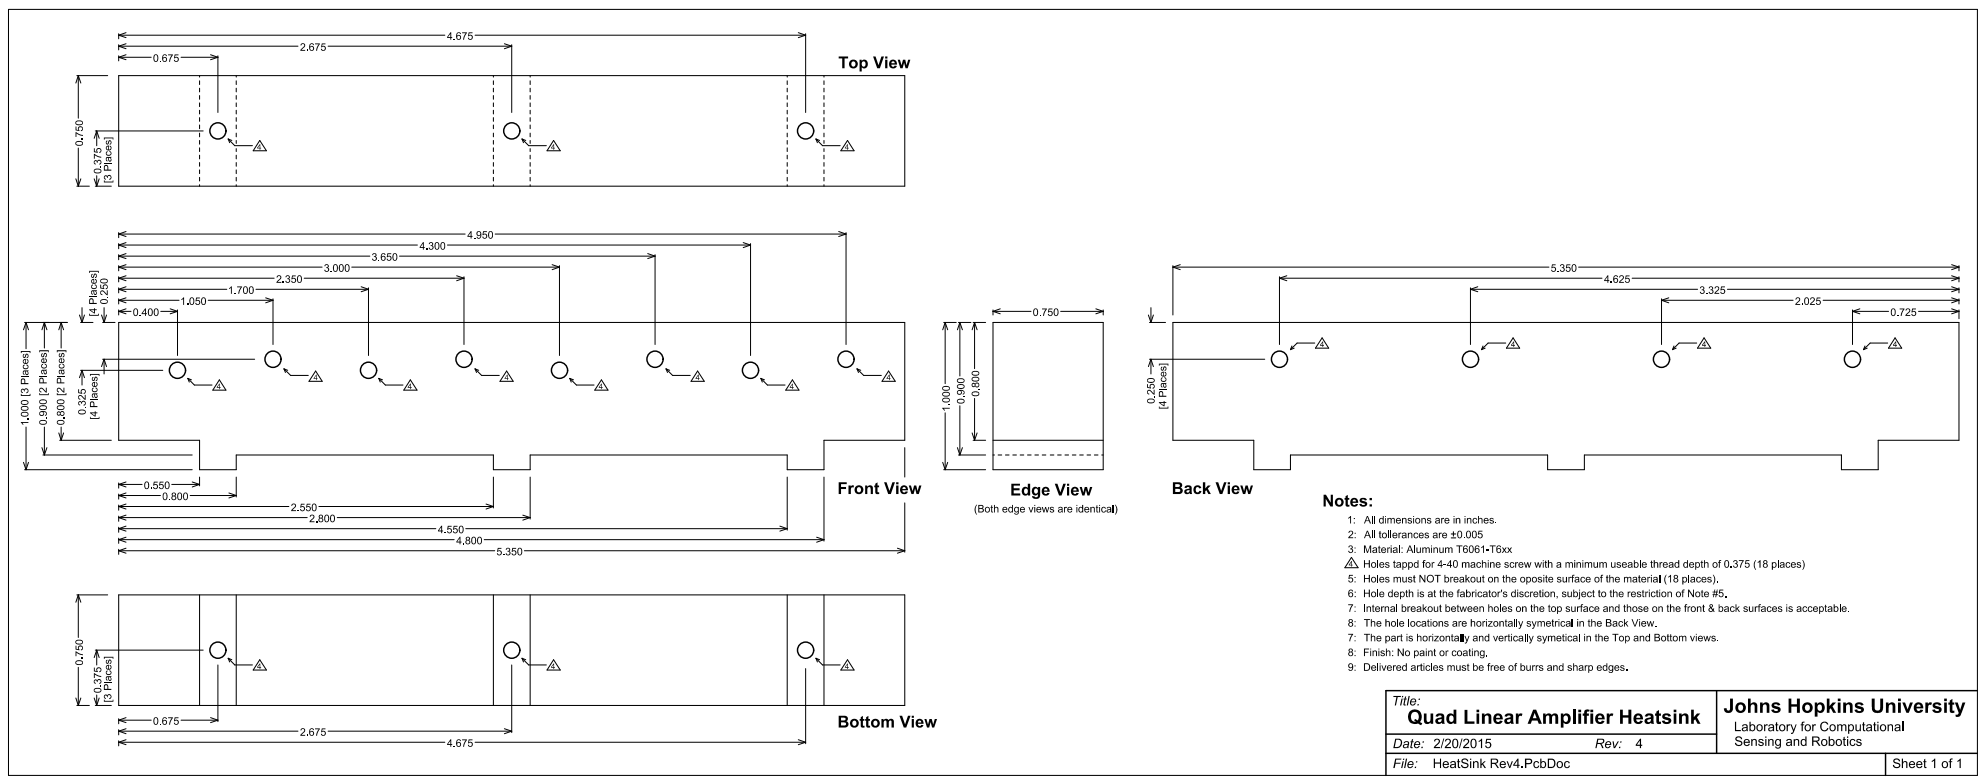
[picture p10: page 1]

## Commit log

2015-01-19 Initial commit, PDF of QLA schematics, Rev 1.1 (5 boards at JHU).
2015-01-19 Design, fab (Gerber), assembly, and BOM files for QLA Rev 1.2
    [QLA-BOM.xls, QLA.PrjPCB, S01.SchDoc, S02.SchDoc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]
2015-01-19 Added PDF of Heatsink drawing (Rev 3 of heat sink); added note about manufacturing change from metric to SAE threaded holes
2015-01-19 Changes for QLA Rev 1.3: changed U31 to 5V relay; swapped pot2 and pot3 on silkscreen; some schematic cleanup.
    [QLA.PrjPCB, S01.SchDoc, S02.SchDoc, S03.SchDoc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]
2015-01-19 BOM for QLA Rev 1.3: changed U31 (relay) and added screwlocks for DB9.
    [QLA-BOM.xls]
2015-01-19 Updated PCB Fabrication (Gerber) and Assembly files for QLA Rev 1.3
2015-01-19 BOM: changed D4 from 15V to 6.8V diode.
    [QLA-BOM.xls]
2015-01-19 Changed R50-51 due to obsolescence; fixed typo in mfg p/n for R62.
    [QLA-BOM.xls]
2015-01-20 Added note about manufacturing change to heatsink drawing
2015-01-20 Updated heat sink drawing and BOM based on build #3 (use of metric screws, rather than SAE)
    [QLA-BOM.xls]
2015-02-21 Updated heatsink to Rev 4; all threads are 4-40
2015-03-02 Updated BOM to use Heat Sink Rev 4; uses 4-40 screws to attach all components to heat sink
    [QLA-BOM.xls]
2015-03-04 Added washer to BOM
    [QLA-BOM.xls]
2015-03-05 Added Avcom part numbers for 3 items
    [QLA-BOM.xls]
2016-02-15 Initial commit for QLA Rev 1.4
    [QLA-BOM.xls, QLA.PrjPCB, S01.SchDoc, S02.SchDoc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]
2018-07-06 BOM updates for Rev1.4a: changed R27, R28, R33, R34; added transorb D12 soldered on back of connector J5
    [QLA-BOM.xls]
2018-07-07 Updated schematics for Rev 1.4a; corrected README.md
    [S01.SchDoc, S02.SchDoc, S03.SchDoc, S04.SchDoc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]
2019-09-30 Changes for Rev 1.4b; increased pot filter cutoff frequency
    [QLA-BOM.xls]
2019-10-01 Updated schematics for Rev 1.4b
    [S01.SchDoc, S02.SchDoc, S03.SchDoc, S04.SchDoc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]
2020-02-06 Changed P/N for Q9-11,15 due to obsolescence; still Rev 1.4b
    [QLA-BOM.xls]
2021-10-17 Updated PCB from SCH (parameter changes only)
    [QLA.PrjPCB]
2021-10-17 Removed R52, R53 from Bessel filter (not needed)
    [QLA-BOM.xls, S09.SchDoc]
2021-10-18 Changed to single VREF and VREF/2 for all channels; added buffer for VREF/2; changed filter cutoff from 60 Hz to 40.8 kHz for motor current provided to ADC. Not yet routed.
    [QLA-BOM.xls, QLA.PrjPCB, S01.SchDoc, S06.SchDoc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]
2021-10-20 Added MAX7317 I/O expander; changed all lib links to QLA.IntLib
    [QLA-BOM.xls, QLA.PrjPCB, S01.SchDoc, S02.SchDoc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]
2021-10-20 Added TMUX1101 analog switches
    [QLA-BOM.xls, S01.SchDoc, S02.SchDoc, S09.SchDoc]
2021-10-20 Changes to visual appearance of S09
    [S09.SchDoc]
2021-10-20 More visual changes to S09
    [S02.SchDoc, S09.SchDoc]
2021-10-29 Schematic changes: added analog mux for selectable voltage gain; added comparators for safety chain and motor supply feedback; updated circuit for Vm/2 (shared between channels)
    [QLA-BOM.xls, QLA.PrjPCB, S01.SchDoc, S02.SchDoc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]
2021-11-04 Added analog mux for motor current range
    [QLA-BOM.xls, S01.SchDoc, S02.SchDoc, S06.SchDoc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]
2021-11-04 Changed Rev parameter from 1.4b to 1.5
    [S01.SchDoc, S02.SchDoc, S03.SchDoc, S04.SchDoc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]
2021-11-13 Simplified design, removing programmable gains
    [S01.SchDoc, S02.SchDoc, S07.SchDoc, S09.SchDoc]
2021-11-22 Finishing schematic
    [QLA-BOM.xls, S01.SchDoc, S02.SchDoc, S06.SchDoc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]
2021-11-22 Updated PCB silkscreen
2021-11-22 Fixed part problems on S07
    [QLA.PrjPCB, S07.SchDoc]
2021-11-22 Minor part updates
    [S07.SchDoc, S09.SchDoc]
2021-11-23 Some layout progress
    [S01.SchDoc, S07.SchDoc, S09.SchDoc]
2021-11-23 Updated R and C values
    [QLA-BOM.xls, S09.SchDoc]
2021-12-07 Fixed split power plane; moved safety fb comparator
2021-12-08 Routed CUR-CTRL and DISABLE-F lines
    [S02.SchDoc]
2021-12-10 Relayout of central section of motor driver; swapped U36A/B
    [S09.SchDoc]
2021-12-11 Added C96; minor layout change in Ch4
    [QLA-BOM.xls, S07.SchDoc]
2021-12-11 Revised SAFETY1-FB schematic
    [QLA-BOM.xls, S07.SchDoc]
2021-12-12 Changed SAFETY1-FB from comparator to transistor; layout improvements; changed 3.48K resistor to 4.02K
    [QLA-BOM.xls, S02.SchDoc, S03.SchDoc, S07.SchDoc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]
2022-02-04 Added Q2 for SAFETY-FB; updated date on silkscreen
    [QLA-BOM.xls, S01.SchDoc, S02.SchDoc, S07.SchDoc]
2022-02-04 Added pads for transorb (D12) on back side of board
    [QLA-BOM.xls, S07.SchDoc]
2022-02-15 Replaced obsolete caps (seq 1,5,7,11,14,16); corrected mfgr for seq 2; corrected P/N for seq 28; added details for new ICs
    [QLA-BOM.xls]
2022-02-15 Consolidated parts in BOM; changed R75-76 to R52-53
    [QLA-BOM.xls, S07.SchDoc]
2022-02-15 Added component counts; improved formatting; other changes
    [QLA-BOM.xls]
2022-02-16 Fixed LTC P/N
    [QLA-BOM.xls]
2022-02-19 EEPROM can be 25LC128 in addition to 25AA128; changed frm H to C temp grade for LT4356
    [QLA-BOM.xls]
2022-02-21 Changed mfgr for Q13,Q14 due to availability
    [QLA-BOM.xls]
2022-02-22 Changed mfgr for dual mosfet Q9-11, Q15
    [QLA-BOM.xls]
2022-03-28 Changed relay footprint for better availability
    [QLA-BOM.xls, S07.SchDoc]
2022-03-28 Changed U32 (2.5V regulator) from SA to SR pinout due to availability
    [QLA-BOM.xls, S09.SchDoc]
2022-04-03 Changed D7 component and footprint due to availability
    [QLA-BOM.xls, S07.SchDoc]
2022-04-03 Changed VHDCI conn due to obsolescence; added screwlocks
    [QLA-BOM.xls]
2022-04-03 Updated 220uF cap and some diodes based on availability
    [QLA-BOM.xls]
2022-04-03 Updated MOSFET and Op Amp for availability
    [QLA-BOM.xls]
2022-04-05 Added LTC2604 and caps, partially routed
    [QLA-BOM.xls, S06.SchDoc]
2022-04-06 Added R75 and level translators for ADCs to schematic and BOM
    [QLA-BOM.xls, S01.SchDoc, S02.SchDoc, S04.SchDoc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]
2022-04-06 Resistor termination for ADC level translation
    [QLA-BOM.xls, S02.SchDoc, S04.SchDoc, S06.SchDoc]
2022-04-08 Finished routing ADC level translators
    [S04.SchDoc, S06.SchDoc]
2022-04-10 Updated part numbers in BOM and schematic
    [QLA-BOM.xls, S04.SchDoc, S06.SchDoc, S09.SchDoc]
2022-04-10 Cleaned up PCB traces
2022-04-11 Restored polygon pours on PCB; minor cleanup of split planes
2022-04-12 Fixed routing of current sense resistor
2022-04-14 Changed R75 to 1K
    [QLA-BOM.xls, S06.SchDoc]
2022-04-18 PCB changes from original designer: extended V-Ref split planes; moved R49; thicker trace to D12; other routing improvements
2022-04-18 Minor updates to PrjPCB file
    [QLA.PrjPCB]
2022-04-19 Updated PCB fabrication and assembly ZIP files for Rev 1.5
2022-04-30 Updated R63 due to obsolescence
    [QLA-BOM.xls]
2022-06-28 Fixed typo in S06 comment (ADC -> DAC)
    [S06.SchDoc]
2022-08-20 Added tristate buffer for Max7317 to schematic and BOM
    [QLA-BOM.xls, S02.SchDoc]
2022-08-20 Rev 1.6: placed and routed tristate buffer
    [S01.SchDoc, S02.SchDoc, S03.SchDoc, S04.SchDoc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]
2022-08-21 Updated U46 info on BOM; updated README.md
    [QLA-BOM.xls]
2022-09-01 Disconnected J2 pin 44 from GND; updated silkscreen to Sept
    [S02.SchDoc]
2022-12-08 Changes to C74; channel C routed
    [S09.SchDoc]
2022-12-08 Finished routing and cleaned up schematic
    [S09.SchDoc]
2022-12-08 Updated C74 on BOM; updated ReadMe.md
    [QLA-BOM.xls]
2022-12-08 Ran design rule check
    [QLA.PrjPCB]
2022-12-09 Updated schematics, fabrication and assembly files for Rev 1.6
2023-01-06 Updated D4 in schematic to match BOM
    [S07.SchDoc]
2023-02-18 Added expected number of boards for build 9
2023-05-05 Updated ADC part number to add Z (ROHS) option
    [QLA-BOM.xls]
